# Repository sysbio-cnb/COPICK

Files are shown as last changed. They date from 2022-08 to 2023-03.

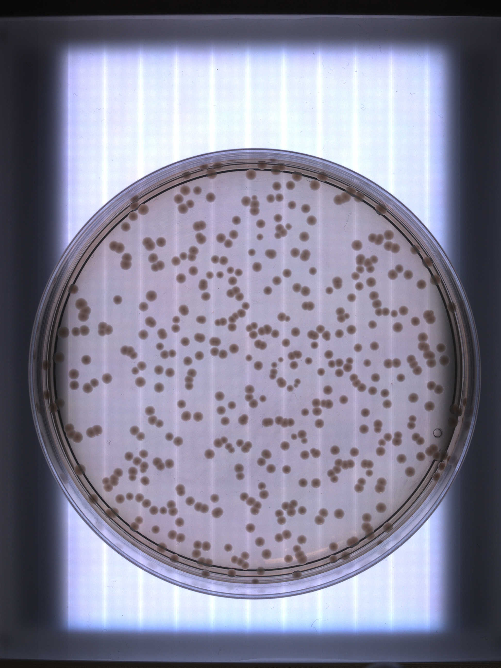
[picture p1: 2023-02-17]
Technical Validation/Raw picking test/ME3I_white__201222_132051.JPG

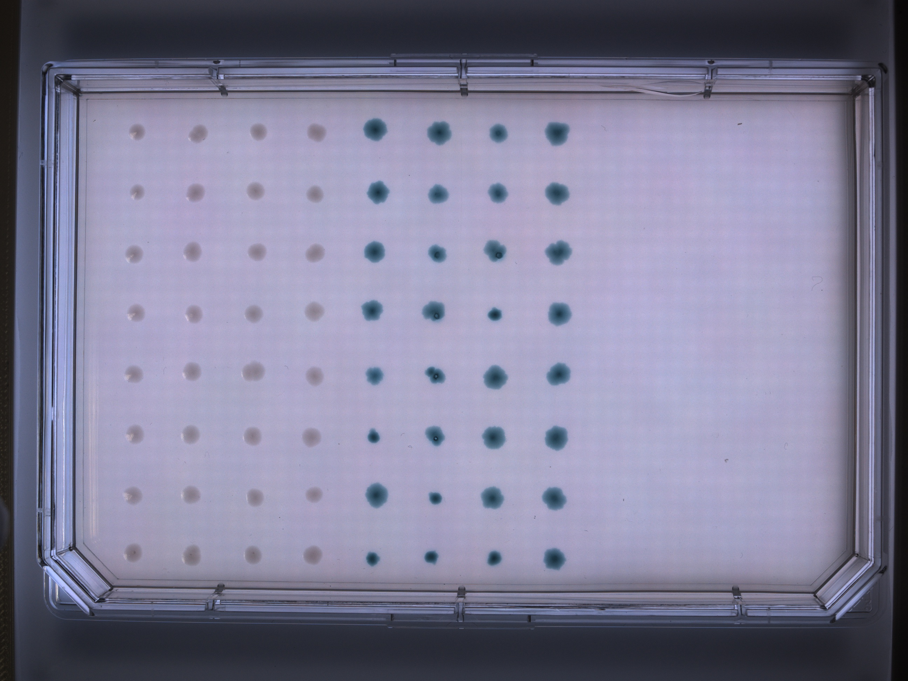
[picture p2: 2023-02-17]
Technical Validation/Color screening test/ME3I_white__310123_132437.JPG

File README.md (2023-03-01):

# COPICK: An open-source adaptation of Opentrons OT-2 robot to support colony picking  
Framework designed to adapt Opentrons 2 robot for colony picking protocols.

Colony picking is a labware based protocol involving the operation of several pieces of hardware in a unique sequence of tasks. The core of such workflow is the visual identification of colonies on the surface of agar plates. Although OT-2 is an open source platform exhibiting great operational capabilities, it lacks of any kind of computer vision recognition system. As a consequence, OT-2 cannot support colony picking.
COPICK package offers a technical solution to enable OT-2 as a colony picking platform at hardware and software level, spotting the two main problems in such task:

-	Computer vision of agar plates is performed using a convolutional neural network with an architecture proposed by Facebook research team (Detectron2, https://github.com/facebookresearch/detectron2), specifically trained with a “de novo” colony plate database. This database contains images of petri dishes with both M9 and LB agar containing P.putida and E.coli colonies.

-	The framework assembly to adapt OT-2 robot for colony picking operations. It includes CAD models for a custom-made scaffolding to assemble a DIY transilluminator (based on a cheap RGB LED matrix powered by a Raspberry Pi) and a high sensitivity USB color camera. The whole setup is complemented with all the scripts required to synchronize the image computation with robot movement and light activation, convert data gathered from the image to actual picking process and use typical filter criterion of colonies (size, color, GFP).

Information about both implementations can be found inside each respective folder.

# Citation

This project is also presented and explained in a formal published manuscript in BioRXiv: https://www.biorxiv.org/content/10.1101/2023.02.28.530165v1

# Contact

Questions and suggestions are kindly welcome. Feel free to contact us on david.rodriguez@cnb.csic.es

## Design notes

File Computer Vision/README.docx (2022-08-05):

COLONY COUNTING AND PICKING PACKAGE FOR OPENTRONS OT-2 (COPICK)

COMPUTER VISION ENGINE

This folder contains a purpose-made software package implementing the computer vision model required to analyze images of agar plates in order to identify bacterial colonies to pick. This package provides the hardware and software designs in different subfolders as described below:

- Light frame CAD designs: contains 3D models to build the photography setup structure for the acquisition of the images for the colony counting and picking dataset (COPICK dataset).
- Detectron2: the core of COPICK image recognition model. It contains the required libraries and scripts to work with a Convolutional Neural Network whose architecture was developed by Facebook research team. It is used to develop an inference model for colonies detection in agar plates. Scripts to set up the configuration for training, evaluation and optimization of the inference model are provided. Additionally, there are scripts to get and visualize model predictions.
- Dataset preparation: contains files related to the COPICK dataset preparation process. Scripts for image processing, segmentation, and automatic annotation and labelling are provided. There is also a *.json file template to be employed during the labelling step (json_template.json) and a *.csv file containing the dataset information (Colony_Picking_database.csv).
- Programs versions.pdf: listed employed programs versions to develop the colony counting and picking system.

DETECTRON2

An inference model for bacterial colonies detection in agar plates was developed using Detectron2, a Facebook AI Research’s library for Computer Vision tasks (https://github.com/facebookresearch/detectron2). It is built for Linux and macOS with Python and it works with PyTorch and torchvision as Machine Learning Framework.

Installation of Detectron2 library for Linux or macOS can be checked here: https://github.com/facebookresearch/detectron2.

Additional instructions on the installation of Detectron2 for Windows are specified in Detectron2_Windows.txt file (in Detectron2 folder). To build the colony detection model, Detectron2 for Windows with CPU only was used. A custom dataset for colony counting and picking purposes (COPICK dataset) was also created to train and evaluate the inference model.

From the different tasks Detectron2 offers, Panoptic Segmentation was chosen mainly because it allows segmentation of every pixel in an image¹. Considering the scenario in which the COPICK dataset is built (colonies are sometimes very numerous, similar and small objects to detect in an image), Panoptic Segmentation was thought to be a good approach in this particular case to get an accurate inference model for bacterial colonies detection. Panoptic Segmentation model and weights previously trained on the COCO dataset (https://cocodataset.org/#home) were used as a starting point. The employed model was the Panoptic R101-FPN (3x) and its corresponding model weights to be found in Detectron2 MODEL ZOO:

https://github.com/facebookresearch/detectron2/blob/main/MODEL_ZOO.md

To prepare and train the COPICK custom dataset, instructions on Detectron2 custom datasets and COCO dataset format for Panoptic FPN Segmentation models were followed:

- Detectron2 custom datasets format:

https://detectron2.readthedocs.io/en/latest/tutorials/datasets.html

- Detectron 2 Panoptic FPN for COCO format:

https://detectron2.readthedocs.io/en/latest/tutorials/builtin_datasets.html

- COCO dataset format:

https://cocodataset.org/#format-data

Overall, to prepare and register a custom dataset with COCO format for a Panoptic FPN model these are the files needed:

- Original images
- Annotations:
  - Panoptic masks (*.png annotations): masks in which every pixel is assigned to a segment in the image (each segment has a unique id).
  - Semantic masks (*.png annotations): refers to the stuff categories in the dataset (isthing=0), i.e. non-colonies objects in the image.
  - Panoptic JSON: includes panoptic segments annotations.
  - Instances JSON: includes things (isthing=1) segments annotations, i.e. colonies in the image.

There are different tools for image annotation and labeling, but the work has to be done manually in most cases for each object in the image. Therefore, traditional image processing techniques were used in order to generate automatic annotations of COPICK dataset. Instructions and scripts to generate the above files are detailed next in DATASET PREPARATION.

DATASET PREPARATION

1. Image acquisition

To prepare the bacterial colony counting and picking dataset (COPICK dataset), a total of 200 petri dishes with different conditions were collected from lab colleagues (Víctor de Lorenzo’s lab, CNB-CSIC). The plates included different bacteria species (either P. putida KT-2440 strain colonies or E. coli) and mediums such as LB or M9 minimal medium. Total number of colonies in each plate were previously counted and added to the plates. Empty plates only with medium were also added.

Before image acquisition, plate preparation data (i.e. agar composition, strain, etc.) was annotated and associated with a plate number. All of this information was stored in a database (Colony_Picking_database.csv, in Dataset preparation folder) containing the following fields:

- date: image capture date.
- id: image number in the dataset.
- filename: assigned name of image using the file_namer.py script in Dataset preparation folder.
- category: 0 for empty plates and 1 for plates with bacterial colonies.
- colonies: number of previously counted colonies in each plate.
- strain: None for empty plates, P. putida or E. coli for the rest of plates.
- medium: M9-cit (minimal M9 citrate medium) or LB.
- multicolor: 0 for plates with non-colored colonies and 1 for plates with colored colonies. This field was added for future additions to the dataset. In this case there were not plates with colored colonies.
- obs: plate observations.
- colonysize: general colonies size in the plate. Small, big or bigger categories.
- recount: number of colonies in plates after recounting some of them.

Image acquisition was performed with a Nikon reflex camera (model D60) with a macro lens (AF-S Micro NIKKOR 60 mm f/2.8G ED). To obtain good quality images, a custom-made illumination device was designed. It was composed by a led circular focus (123 mm, 6.7w, 1000 lumen) supported by a 3D holder designed using Autodesk Inventor Professional (2015) and printed with a Ultimaker³ 3D printer (see Figure 1). Two light diffusing layers of translucid plastic and paper were added to the assembly in order to attenuate the amount of light. Both 3D models can be found in the Light frame CAD designs folder.

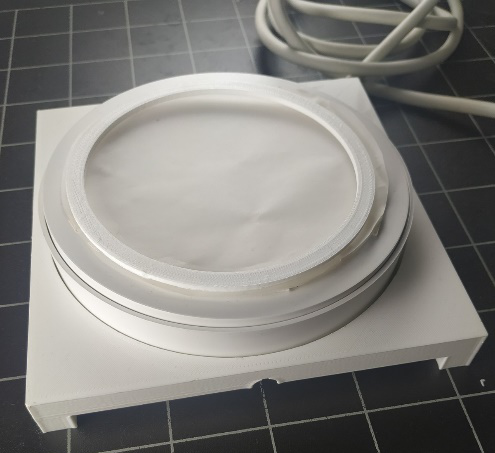
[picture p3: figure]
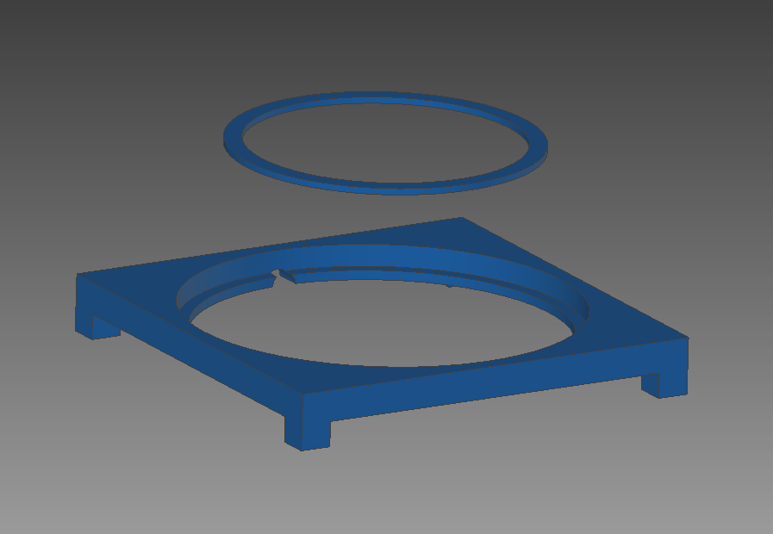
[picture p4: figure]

Figure 1. Led focus support structure and plates ring holder. a) 3D pieces design; b) final structure for image acquisition.

a

b

Images of the 200 collected plates were taken under the same conditions without lid for to avoid lines and reflections in the images.

2. Dataset augmentation

After image acquisition, dataset augmentation techniques were applied in order to increase the dataset size. Using the augmentation_stage.py script (in Dataset preparation folder), flip and rotation transformations were applied to the original set of images generating 15 replicas of each one and resulting in a total of 3000 images in the COPICK dataset. Every image was assigned a different name using the file_namer.py script (in Dataset preparation folder) during the augmentation process. Replicas of the same image share a common code at the beginning of their names for a better identification:

Code → A0000X, where the X corresponds to the assigned number of plate during image acquisition. Therefore, X values range from 1 to 200.

The 3000 images were divided in two subsets: train dataset (2250 images) and val dataset (750 images) for training and validation steps respectively. Previously mentioned database file (Colony_Picking_database.csv) contains the information of the whole augmented COPICK dataset.

3. Image processing and annotation

In order to produce panoptic and semantic annotations for each image in the dataset (as mentioned previously), two specific scripts (PROCESS_DATASET_PANOPTIC_SEGMENTATION.py and PROCESS_DATASET_INSTANCE_SEGMENTATION.py) and auxiliary functions were created (see Dataset preparation folder).

First, PROCESS_DATASET_PANOPTIC_SEGMENTATION.py was executed. In this script, the steps are:

1. Define dataset images paths and choose train or val datasets to be processed.
2. Then load and set fields to the provided json_template.json file (-json and csv files- folder in Dataset preparation folder) to store panoptic annotations.
3. Access database data (Colony_picking_database.csv in -json and csv files- in Dataset preparation folder) for panoptic segments annotations.
4. Define color combinations for panoptic *.png annotations.
5. Process dataset (train or val) to get panoptic annotations.
  5.1. Load images and create new folders to store panoptic *.png annotations.
  5.2. Call image_pretreatment.py function (in Dataset preparation folder) to crop images in order to avoid unnecessary regions and get region-based masks and data to be used in next segmentation steps.
  5.3. Call segmentation_stage.py function (in Dataset preparation folder) to generate final segmented panoptic masks *.png annotations.
  5.4. Store panoptic masks *.png annotations.
  5.5. Get panoptic segments annotations and store them in the json_template. Then save the *.json annotation file to specified folder.
6. Process dataset (train or val) to get semantic *.png annotations from panoptic *.png annotations.
  6.1. Access panoptic annotations (both *.png and *.json files) and create new paths to store semantic annotations.
  6.2. Define dataset categories and call modified Detectron2 function separate_semantic_from_panoptic.py (in Dataset preparation) to get and store semantic masks *.png annotations.

Then, PROCESS_DATASET_INSTANCE_SEGMENTATION.py script was executed to generate instances annotations. In this script the steps are:

1. Choose train or val dataset to process and load previously created panoptic *.json annotations.
2. Then load and set fields to the provided json_template.json file (-json and csv files- folder in Dataset preparation folder) to store instance annotations.
3. Process dataset (train or val) to get instance annotations from panoptic info.
4. Get instances annotations and store them in the json_template. Then save the *.json annotation file to specified folder.

Further explanation on each mentioned function can be found inside its respective script in the Dataset preparation folder.

DATASETS DESCRIPTION

COPICK dataset images and annotations files as well as some trial smaller datasets can be found in this repository to download:

https://sysbiol.cnb.csic.es/EMBBT

In the repository, the -Complete dataset (COPICK)- folder contains the images and annotations of the whole colony counting and picking dataset used to generate the final trained model on Detectron2 for bacterial colonies detection in agar plates. The original images from the whole dataset are stored and separated in "train" and "val" folders. The corresponding annotations of both datasets follow the Panoptic Segmentation format for Detectron2 with COCO dataset and PanopticFPN models previously described:

- *.json files for both panoptic and instances annotations: generated with -PROCESS_DATASET_PANOPTIC_SEGMENTATION.py- and -PROCESS_DATASET_INSTANCES_SEGMENTATION.py- scripts respectively (in Dataset preparation folder).
- *.png panoptic masks annotations: generated with -PROCESS_DATASET_PANOPTIC_SEGMENTATION.py- script (in Dataset preparation folder). Created for train and val datasets in -panoptic_trainval (panoptic annotations)- folder.
- *.png semantic mask annotations: generated from panoptic masks annotations with modified Detectron2 -prepare_panoptic_fpn.py- script (inside -PROCESS_DATASET_PANOPTIC_SEGMENTATION.py- script (in Dataset preparation folder). Created for train and val datasets in panoptic_stuff (semantic annotations) folder.

There is also a "Trial datasets" folder including smaller samples of the whole dataset following the same format as the complete dataset. These datasets are created in order to do faster testing with data. The folder includes:

- train_val_short: contains 10 training images and 3 validation images and corresponding annotations files.
- train_val_test_sample: contains 160 training images and 40 validation images and corresponding annotations files.
- val_short: contains 1 image for inference/validation only and corresponding annotations files.

DETECTRON2 CONFIGURATION

Some examples on Detectron2 configuration for training, evaluation and inference can be found in here:

https://colab.research.google.com/drive/16jcaJoc6bCFAQ96jDe2HwtXj7BMD_-m5

As Panoptic Segmentation is a relatively new task, there is not much available information nor examples on how to set up the configuration for training and evaluation purposes on custom datasets. Here is a list of additional resources that were consulted in order to set up Detectron2 to train with the COPICK dataset:

- Train Panoptic Segmentation model on custom dataset:

https://github.com/facebookresearch/detectron2/issues/1691

- Panoptic Segmentation dataset organization:

https://github.com/facebookresearch/detectron2/issues/1201#issuecomment-879864483

- Dataset registration:

https://github.com/facebookresearch/detectron2/issues/327

- Load custom datasets for evaluation:

https://github.com/facebookresearch/detectron2/issues/552

Additionally, based on information from the above sites and personal experience, changes were applied to some of the Detectron2 package scripts. Those can be found in -Changes in Detectron2 scripts.txt- file (in Detectron2 folder).

Detectron2 configuration setup scripts for training, evaluation, inference and optimization procedures are provided and detailed down below.

1. Training and Evaluation

Detectron2 configuration to train and evaluate the inference model on the COPICK dataset can be found in detectron2_train_eval.py script (in Train, evaluation and optimization folder from the Detectron2 folder). In this script, both train and val datasets are first registered with -register_coco_panoptic_separated- function from Detectron2. For the register, corresponding images and annotations files are required. After that, training configuration parameters are set to train the inference model on the COPICK dataset. Then, trained model weights are stored and evaluation parameters are set for evaluation, obtaining Panoptic Segmentation metrics (see https://cocodataset.org/#panoptic-eval).

2. Model Inference

Model inference can be done in different ways to check model predictions. Additionally to Detectron2 Visualizer function for registered datasets, scripts to get predicted colonies in the images and visualize them were created:

- detectron2_get_model_predictions.py: it is used to get predictions from the trained model and store them. Dataset registration is only necessary if Detectron2 Visualizer function is going to be used. If not, then just the trained model and weights as well as the test parameters are required to set the model predictor for inference. After that, multiple or single images can be processed in order to get and store panoptic predictions.
- display_colonies_overlay.py: it is used to process panoptic predictions to get only the colonies footprint and display an overlay of it on top of the original image for visualization purposes.

Both scripts can be found in the -Train, evaluation and optimization- folder (inside Detectron2 folder).

3. Hyperparameters optimization

To search for best hyperparameters combinations and improve the colony detection model accuracy, hyperparameter optimization techniques were used. For that purpose, the Optuna library was chosen (https://optuna.org/). By default, this library uses Bayesian Optimization algorithms but it can be changed if wanted.

The script -detectron2_optimization.py- (in Train, evaluation and optimization- folder from Detectron2 folder) is provided to perform hyperparameters optimization. The configuration of parameters values was done following Optuna’s instructions. In this case, the parameters to be optimized were:

- SOLVER.IMS_PER_BATCH: defined as number of images per batch across all machines.
- SOLVER.BASE_LR: learning rate.
- SOLVER.MAX_ITER: maximum number of iterations.
- MODEL.ROI_HEADS.BATCH_SIZE_PER_IMAGE: number of regions of interest per image during training.

Further information on Detectron2 configuration parameters can be found in here:

https://detectron2.readthedocs.io/en/latest/modules/config.html

Parameters to be optimized had to be included inside a function along with Detectron2 necessary configuration parameters for training and evaluation. This function returns a Panoptic Segmentation metric value SQ (Segmentation Quality) after evaluation to be maximized. The higher the SQ value is, the better the combination of hyperparameters of that optimization iteration are supposed to be to train the colony detection model and get more accurate predictions. Initially, PQ (Panoptic Quality) metric was used for optimization but better results were observed with SQ.

The hyperparameter optimization was performed by executing runs of 6 trials (n_trials) followed by the addition of the results to a *.pkl file as described in Optuna library to increase the number of data points in each batch and improve the accuracy of the next prediction. The reason of such procedure was a recurrent memory error that systematically interrupted the execution of larger optimization runs. We hypothesize that the issue is located at some point of inner memory allocation managed by torch libraries required to execute Detectron.

Once optimization was finished, best trained model weights both for PQ and SQ parameters were selected. These weights are provided in the above mentioned repository along with the COPICK dataset files.

LIMITATIONS AND ISSUES

Limitations about use, configuration and performance of the presented inference model are described next:

- Documentation: public documentation provided by both Detectron2 and COCO dataset regarding Panoptic Segmentation was found to be confusing at some points. The lack of information and examples on how to train Panoptic Segmentation models on custom datasets made it difficult to set the final configuration to train and evaluate our model and we ended up using a mix of different sources as mentioned before.
- COPICK dataset: the COPICK dataset was built using the most common conditions for plates preparation in the lab they were collected from. Those are not representative of other conditions and it has to be considered, even though Neural Networks models are very versatile and can discriminate different types of similar objects under variable circumstances. Also, light settings for image acquisition in the dataset are very important for a good image quality and we found our model to be very sensitive to light conditions when changing them inside the Opentrons robot. Finally, we considered the dataset size to be appropriate as a starting point. However, images with previously unincluded information such as different mediums or colonies fluorescence, color, and shape, as well as extra information on colonies size and number (regarding more information of groups of 2 or more colonies too), would be required to increase the dataset data and variability for the model to learn from and be more complete in the future.
- Image segmentation: image segmentation was probably the main problem to tackle when preparing the COPICK dataset annotations. We had to deal with difficult regions such as the border of the plates where the plastic is thicker and both the agar and the colonies often have a different morphology. Moreover, the agar is not a homogeneous medium: it has bubbles, wrinkles or traces of particles that add unspecific noise to the apparent uniformity of the plate. Therefore, light conditions vary in those regions even for the same agar composition. Additionally, plates with very small and hundreds of colonies had to be treated differently for a higher contrast of the colonies in the images in order to detect them. For those reasons, we had to consider all of the possible regions and cases to create the segmentation algorithm. We managed to segment as many colonies as possible in the dataset images, including the problematic ones, still the segmentation was not perfect as it is not a trivial task to perform and it conditioned the posterior model training.
- Memory usage: recurrent memory errors were found at some point during the inference model training and evaluation process and also during hyperparameters optimization. For the installation of Detectron2 and Pytorch we could not manage to set it up for GPU usage and therefore had to use only the CPU. This problem, as well as the inner memory allocation of torch libraries mentioned before, were limitations to build the inference model.
- Model inference results: after several training and optimization runs of the model, we observed it was good at segmentation but not that much at identification. This means it was accurate when segmenting every different object in an image, mainly varying on the contours of the segments from one training to another, but it worked worse when assigning a category to those segmented objects, in this case, the colonies. Hence, model predictions have some colonies classified as colonies and the rest only segmented and uncategorized. For our purposes, this is not a problem as we get the segmentation footprint of the colonies in the images anyway and that is enough to identify them and pick them. For the implementation of the colony picking application in the Opentrons, we ended up using a combination of the best trained model weights to get the best segmentation results possible.
- Model metrics: during evaluation, we found Panoptic Segmentation metrics to fail for the stuff categories as every metric value was always 0. We tried to solve this issue but we could not figure out what was causing it. Also, we observed during optimization that larger values of both PQ and SQ metrics were not necessarily correlated with a realistic prediction of colonies in the images at naked eye. As Panoptic Segmentation codes for evaluation task provided by COCO are relatively new and have been only tested on the COCO dataset (check https://cocodataset.org/#panoptic-eval), evaluation metrics and configuration might not be working well for our custom dataset and model.

REFERENCES

1. Panoptic Segmentation task paper: https://arxiv.org/abs/1801.00868

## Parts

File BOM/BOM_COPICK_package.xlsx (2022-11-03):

Concept | Supplier | Ref | Units
Raspberry Pi 4B , 8GB, bulk | Mouser | 358-RPI4MODBP8GBBULK | 1
USB 3.0 Micro-B to Type-A Locking Cable, 3m | Edmund Optics | #14-903 | 1
Hoya Y50 (500nm), 25.4mm Dia., 2.5mm Thick, Colored Glass Longpass Filter | Edmund Optics | #66-050 | 1
Allied Vision Alvium 1800 U-500c, 1/2.5" 5.0MP C-Mount, Right Angle USB 3.1 Color Camera | Edmund Optics | #14-131 | 1
12mm UC Series Fixed Focal Length Lens | Edmund Optics | #33-303 | 1
Mount M25.5 x 0.5 for 25/25.4mm Diameter Filters | Edmund Optics | #65-800 | 1
64X32 RGB LED MATRIX - 2.5MM PIT | Digikey | 1528-5036-ND | 1
5V AC/DC Externo Escritorio (Clase II) Adaptador Cable Entrada | Digikey | 1528-1466AD-ND | 1
6.00' (1.83m) Cable de alimentación Negro CEE 7/16 a IEC 320-C7 SPT-2 | Digikey | T1167-EU-ND | 1
LED MATRIX RGB HAT RTC RASP PI | Digikey | 1528-1432-ND | 1
MINI-MAGNET FEET FOR RGB LED MAT | Digikey | 1528-4631-ND | 1
3D printed parts | - | -
M3 screws (12 mm) | RS amidata | 190-456 | 1
M3 nuts | RS amidata | 189-563 | 1
M4 screws (20 mm) | RS amidata | 227-6849 | 1
M4 nuts | RS amidata | 189-579 | 1
Bosch Rexroth Connecting Component, Angle Bracket, strut profile 20 mm, groove Size 6mm | RS amidata | 466-7354 | 1
Light diffusor: PETG or PE plate , 5 mm width | - | - | 1
Light diffusor 2: PETG or PE plate , 5 mm width | - | - | 1
CAT 5 / CAT 6 Ethernet cable | Digikey | AE10365-ND | 1
8 port switch, TP-link TL-SG108E | Amazon | TL-SG108E | 1
wall charger usb 3.0, 2A | Amazon |  | 1
16 GB SD card | Amazon |  | 1

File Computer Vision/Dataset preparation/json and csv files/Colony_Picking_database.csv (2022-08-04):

date | id | filename | category | colonies | strain | medium | multicolor | obs | colonysize | recount
16/09/2021 | 1 | A0000125pa5gr2idie3f2bv4kupalr1.jpg | 0 | 0 | None | M9_cit | 0 |  | big
16/09/2021 | 2 | A000015fnp53868wk181oa8q35bhdfj.jpg | 0 | 0 | None | M9_cit | 0 |  | big
16/09/2021 | 3 | A000017blexsmxpoldrkko23xwipyb0.jpg | 0 | 0 | None | M9_cit | 0 |  | big
16/09/2021 | 4 | A00001bgvr54etcrd66lmu3dhparv5a.jpg | 0 | 0 | None | M9_cit | 0 |  | big
16/09/2021 | 5 | A00001cvlner9f6ccik1m3yzgx7euby.jpg | 0 | 0 | None | M9_cit | 0 |  | big
16/09/2021 | 6 | A00001g55zyv68qmezpfr794x4itvl6.jpg | 0 | 0 | None | M9_cit | 0 |  | big
16/09/2021 | 7 | A00001gxaz519m72og3gcu8e3wbg2x7.jpg | 0 | 0 | None | M9_cit | 0 |  | big
16/09/2021 | 8 | A00001ifallx9e1vcrpj0xz2v2l1bvc.jpg | 0 | 0 | None | M9_cit | 0 |  | big
16/09/2021 | 9 | A00001mre7wa8a446zoo3rdja20u31s.jpg | 0 | 0 | None | M9_cit | 0 |  | big
16/09/2021 | 10 | A00001qtv38wa1q83zlr5pooi141w1s.jpg | 0 | 0 | None | M9_cit | 0 |  | big
16/09/2021 | 11 | A00001sz8bqkzq0zr17lmxunfps6ii2.jpg | 0 | 0 | None | M9_cit | 0 |  | big
16/09/2021 | 12 | A00001w7halk3oyksxyvznr5q3vem3y.jpg | 0 | 0 | None | M9_cit | 0 |  | big
16/09/2021 | 13 | A00001wezej7ya386otummtlp9r6cru.jpg | 0 | 0 | None | M9_cit | 0 |  | big
16/09/2021 | 14 | A00001xaznw266ws5k6cgpv5f7s8bty.jpg | 0 | 0 | None | M9_cit | 0 |  | big
16/09/2021 | 15 | A00001yxv8zs82ltzsjoyv6see0uzq9.jpg | 0 | 0 | None | M9_cit | 0 |  | big
16/09/2021 | 16 | A000021brca8pix0p1475vr33a17k5u.jpg | 1 | 91 | P. putida | M9_cit | 0 |  | big
16/09/2021 | 17 | A0000231324ioer85ijegxmg743lynn.jpg | 1 | 91 | P. putida | M9_cit | 0 |  | big
16/09/2021 | 18 | A000023ls3ta6ttl0iw7gp83msg57e6.jpg | 1 | 91 | P. putida | M9_cit | 0 |  | big
16/09/2021 | 19 | A000025huv9kxjn3hza0xxqhslwt4tc.jpg | 1 | 91 | P. putida | M9_cit | 0 |  | big
16/09/2021 | 20 | A000027zrqi3aezz9lt2siq9bohwc1u.jpg | 1 | 91 | P. putida | M9_cit | 0 |  | big
16/09/2021 | 21 | A00002c5lj73313kpz424rsuq10e4q8.jpg | 1 | 91 | P. putida | M9_cit | 0 |  | big
16/09/2021 | 22 | A00002d2kilfobrbq5erai8pm2nczjb.jpg | 1 | 91 | P. putida | M9_cit | 0 |  | big
16/09/2021 | 23 | A00002eu1a3ge3aj789mj2eh8akqsnt.jpg | 1 | 91 | P. putida | M9_cit | 0 |  | big
16/09/2021 | 24 | A00002gfkyesf41a8ujvz2gcisccghz.jpg | 1 | 91 | P. putida | M9_cit | 0 |  | big
16/09/2021 | 25 | A00002h8ahvgqjvwi5bgns6dtg5mvg5.jpg | 1 | 91 | P. putida | M9_cit | 0 |  | big
16/09/2021 | 26 | A00002hz0y2816vvoq3n15b63cb3r95.jpg | 1 | 91 | P. putida | M9_cit | 0 |  | big
16/09/2021 | 27 | A00002o8nzisdk3og1lgybj9nul7m2m.jpg | 1 | 91 | P. putida | M9_cit | 0 |  | big
16/09/2021 | 28 | A00002pexrmshcmz9fzknj9c2y0pbxq.jpg | 1 | 91 | P. putida | M9_cit | 0 |  | big
16/09/2021 | 29 | A00002s6w3asd0zikiqqovcobhgxsu8.jpg | 1 | 91 | P. putida | M9_cit | 0 |  | big
16/09/2021 | 30 | A00002t4lgaor1idwmcnbi8oryhz8ri.jpg | 1 | 91 | P. putida | M9_cit | 0 |  | big
16/09/2021 | 31 | A000032ymuivkqisok7bm7891ztwntg.jpg | 1 | 67 | P. putida | M9_cit | 0 |  | big
16/09/2021 | 32 | A0000374xgg3faz8ut9x8f6aczsb6qh.jpg | 1 | 67 | P. putida | M9_cit | 0 |  | big
16/09/2021 | 33 | A0000395f2kwbakbi86kip7z0cwggr9.jpg | 1 | 67 | P. putida | M9_cit | 0 |  | big
16/09/2021 | 34 | A00003aorrz6rcrujqomgfuv6fouedk.jpg | 1 | 67 | P. putida | M9_cit | 0 |  | big
16/09/2021 | 35 | A00003cu8bvasxy3lp20k4n38s869bj.jpg | 1 | 67 | P. putida | M9_cit | 0 |  | big
16/09/2021 | 36 | A00003g04g2zppox5vhxbqu7tosb67a.jpg | 1 | 67 | P. putida | M9_cit | 0 |  | big
16/09/2021 | 37 | A00003g4yhn60qh7xjws63nx556gg4x.jpg | 1 | 67 | P. putida | M9_cit | 0 |  | big
16/09/2021 | 38 | A00003jbotnyz71n5t7xv4acuthk7u1.jpg | 1 | 67 | P. putida | M9_cit | 0 |  | big
16/09/2021 | 39 | A00003kezhrbni3j1h5gj8atr6h850t.jpg | 1 | 67 | P. putida | M9_cit | 0 |  | big
16/09/2021 | 40 | A00003kqah2dnhuiiknxlefynu79fsr.jpg | 1 | 67 | P. putida | M9_cit | 0 |  | big
16/09/2021 | 41 | A00003l9jtmyozxsxcr4c7f4o7tsj3x.jpg | 1 | 67 | P. putida | M9_cit | 0 |  | big
16/09/2021 | 42 | A00003mrs477xdbh95su65uvpr7euo1.jpg | 1 | 67 | P. putida | M9_cit | 0 |  | big
16/09/2021 | 43 | A00003npkb798j1i5nn0evttn6wmlwh.jpg | 1 | 67 | P. putida | M9_cit | 0 |  | big
16/09/2021 | 44 | A00003nrk93x3oosyeb151gmzmvinui.jpg | 1 | 67 | P. putida | M9_cit | 0 |  | big
16/09/2021 | 45 | A00003yg3tagqbshz716acr2w9wfxwg.jpg | 1 | 67 | P. putida | M9_cit | 0 |  | big
16/09/2021 | 46 | A000042hhjzcwvflnjxzktp0is7ps99.jpg | 1 | 44 | P. putida | M9_cit | 0 |  | big
16/09/2021 | 47 | A0000437ugpshij4g5vsrnlno8wuufs.jpg | 1 | 44 | P. putida | M9_cit | 0 |  | big
16/09/2021 | 48 | A000044d9jqi8hq7zaeu8ibigm9s418.jpg | 1 | 44 | P. putida | M9_cit | 0 |  | big
16/09/2021 | 49 | A000044e1qrgd3sa1hqr4a7mi7m54yb.jpg | 1 | 44 | P. putida | M9_cit | 0 |  | big
16/09/2021 | 50 | A000046dfkyg6t78mnbk4iyxoda93h0.jpg | 1 | 44 | P. putida | M9_cit | 0 |  | big
16/09/2021 | 51 | A0000482je8nzs00hz4e595r0p0b3m2.jpg | 1 | 44 | P. putida | M9_cit | 0 |  | big
16/09/2021 | 52 | A000049r7jflirf4mq6x8dnomlogj5a.jpg | 1 | 44 | P. putida | M9_cit | 0 |  | big
16/09/2021 | 53 | A00004an08qaig3t867aj8vu3kp51f8.jpg | 1 | 44 | P. putida | M9_cit | 0 |  | big
16/09/2021 | 54 | A00004ga5xno45lsqdqwoevjvyr3xjf.jpg | 1 | 44 | P. putida | M9_cit | 0 |  | big
16/09/2021 | 55 | A00004gijackmbgpe2nc0adu2gu1tyq.jpg | 1 | 44 | P. putida | M9_cit | 0 |  | big
16/09/2021 | 56 | A00004jzaaaer9h64dyvmgam3tx9b4z.jpg | 1 | 44 | P. putida | M9_cit | 0 |  | big
16/09/2021 | 57 | A00004m6kwbwc0g92iqql2hn9f4bvq9.jpg | 1 | 44 | P. putida | M9_cit | 0 |  | big
16/09/2021 | 58 | A00004u95rhb57ran6lu1nbi0lfdbt1.jpg | 1 | 44 | P. putida | M9_cit | 0 |  | big
16/09/2021 | 59 | A00004ylrp7ok6kurz6jl8qa97kqe1h.jpg | 1 | 44 | P. putida | M9_cit | 0 |  | big
16/09/2021 | 60 | A00004z5e1ir6lttwwbdejkvo7p2bky.jpg | 1 | 44 | P. putida | M9_cit | 0 |  | big
16/09/2021 | 61 | A000050342kk9oekqj7twtarskonerp.jpg | 1 | 85 | P. putida | M9_cit | 0 |  | big
16/09/2021 | 62 | A000050i6x8vel5xk7r3p2zlc3uk93s.jpg | 1 | 85 | P. putida | M9_cit | 0 |  | big
16/09/2021 | 63 | A000052j5t6fggvnd4idya6l5li4bqs.jpg | 1 | 85 | P. putida | M9_cit | 0 |  | big
16/09/2021 | 64 | A000056mijhp79eao8lza8w0qejw9po.jpg | 1 | 85 | P. putida | M9_cit | 0 |  | big
16/09/2021 | 65 | A00005a75fp8l23fzcvo6w4qm37423i.jpg | 1 | 85 | P. putida | M9_cit | 0 |  | big
16/09/2021 | 66 | A00005d9s6bej7g9ngl2oo3e0zjfvh1.jpg | 1 | 85 | P. putida | M9_cit | 0 |  | big
16/09/2021 | 67 | A00005f5flv8idwruz42iadtk1bl6ai.jpg | 1 | 85 | P. putida | M9_cit | 0 |  | big
16/09/2021 | 68 | A00005f88s7oipyct4024qqpv1h9a9r.jpg | 1 | 85 | P. putida | M9_cit | 0 |  | big
16/09/2021 | 69 | A00005glwuv5q1tx884t0a1nf85b2k4.jpg | 1 | 85 | P. putida | M9_cit | 0 |  | big
16/09/2021 | 70 | A00005s95dzw3215dyctjmt83j8n1ho.jpg | 1 | 85 | P. putida | M9_cit | 0 |  | big
16/09/2021 | 71 | A00005vs0kxztnehei6iw2o09s7aros.jpg | 1 | 85 | P. putida | M9_cit | 0 |  | big
16/09/2021 | 72 | A00005w5fnqtr7luw2rr8zmumg9z6ay.jpg | 1 | 85 | P. putida | M9_cit | 0 |  | big
16/09/2021 | 73 | A00005wijjqw57hrot0oiy5m0dil7qy.jpg | 1 | 85 | P. putida | M9_cit | 0 |  | big
16/09/2021 | 74 | A00005xyo7dw6j2vjsj7ej0136v6fbz.jpg | 1 | 85 | P. putida | M9_cit | 0 |  | big
16/09/2021 | 75 | A00005y06r1a339ujnia2bsui16l9vh.jpg | 1 | 85 | P. putida | M9_cit | 0 |  | big
16/09/2021 | 76 | A0000615xod6tfueju6ek0szasbcu13.jpg | 1 | 115 | P. putida | M9_cit | 0 |  | big
16/09/2021 | 77 | A000061c4alfy0mzbb3i7ehxtv3vht5.jpg | 1 | 115 | P. putida | M9_cit | 0 |  | big
16/09/2021 | 78 | A000061ow6v7kmqm1dh34cocrowkddu.jpg | 1 | 115 | P. putida | M9_cit | 0 |  | big
16/09/2021 | 79 | A000063pz404fdu9oixn71n4r8rq5td.jpg | 1 | 115 | P. putida | M9_cit | 0 |  | big
16/09/2021 | 80 | A000065452lf4lj85f8go2qmahtkzow.jpg | 1 | 115 | P. putida | M9_cit | 0 |  | big
16/09/2021 | 81 | A000066xbkxe54pn8c2iujqdkd4ucum.jpg | 1 | 115 | P. putida | M9_cit | 0 |  | big
16/09/2021 | 82 | A000069nkdxkv5gnxm8n0x1sfmaye04.jpg | 1 | 115 | P. putida | M9_cit | 0 |  | big
16/09/2021 | 83 | A00006bgsulgrg4359gv3shhpjfoymd.jpg | 1 | 115 | P. putida | M9_cit | 0 |  | big
16/09/2021 | 84 | A00006ckv6jnf8l3ibh2z91ecpzdzqb.jpg | 1 | 115 | P. putida | M9_cit | 0 |  | big
16/09/2021 | 85 | A00006jr2i3a0u8f2b7zcups6zlewxn.jpg | 1 | 115 | P. putida | M9_cit | 0 |  | big
16/09/2021 | 86 | A00006kwizdvby50c150s9tuo3xqbbb.jpg | 1 | 115 | P. putida | M9_cit | 0 |  | big
16/09/2021 | 87 | A00006qex7u5f2vazey59cfs9u75v3a.jpg | 1 | 115 | P. putida | M9_cit | 0 |  | big
16/09/2021 | 88 | A00006uh6iw34gt54uekvy2fp905eb4.jpg | 1 | 115 | P. putida | M9_cit | 0 |  | big
16/09/2021 | 89 | A00006w8eab1yk8a8iodfev4byz1ylg.jpg | 1 | 115 | P. putida | M9_cit | 0 |  | big
16/09/2021 | 90 | A00006zohsu6su3h4pj9ljx73ozotj0.jpg | 1 | 115 | P. putida | M9_cit | 0 |  | big
16/09/2021 | 91 | A0000700szxmpryrtmkma7a0xr2u26v.jpg | 1 | 1 | P. putida | M9_cit | 0 |  | big
16/09/2021 | 92 | A000073hul1rhn14iita59rfzi4bgb4.jpg | 1 | 1 | P. putida | M9_cit | 0 |  | big
16/09/2021 | 93 | A000074dpl4uyihwqb8rnx1o7kwd6oo.jpg | 1 | 1 | P. putida | M9_cit | 0 |  | big
16/09/2021 | 94 | A000079ygs7q7lhf0q3sz03xwhss7lc.jpg | 1 | 1 | P. putida | M9_cit | 0 |  | big
16/09/2021 | 95 | A00007e3vllczp2t624gmpqfstd2k8b.jpg | 1 | 1 | P. putida | M9_cit | 0 |  | big
16/09/2021 | 96 | A00007gokdd3b2unkdky613imgg5w7f.jpg | 1 | 1 | P. putida | M9_cit | 0 |  | big
16/09/2021 | 97 | A00007hb846e2on6i4mnc1u03fd8qir.jpg | 1 | 1 | P. putida | M9_cit | 0 |  | big
16/09/2021 | 98 | A00007jyph6tawkyor43s0ohrd8ksi4.jpg | 1 | 1 | P. putida | M9_cit | 0 |  | big
16/09/2021 | 99 | A00007ly6rfdixi73ee4tr3ey6vlwai.jpg | 1 | 1 | P. putida | M9_cit | 0 |  | big
16/09/2021 | 100 | A00007mt2z19t1qyv4209ic1a6xq5hd.jpg | 1 | 1 | P. putida | M9_cit | 0 |  | big
16/09/2021 | 101 | A00007ncq16nc67aqpyfu1h589tls2s.jpg | 1 | 1 | P. putida | M9_cit | 0 |  | big
16/09/2021 | 102 | A00007q8cngkmb99etdsl6kyax5phbi.jpg | 1 | 1 | P. putida | M9_cit | 0 |  | big
16/09/2021 | 103 | A00007vkv0ytaady1vtdbnn2kn0oupn.jpg | 1 | 1 | P. putida | M9_cit | 0 |  | big
16/09/2021 | 104 | A00007ybnnsgt7dtcpvtd9mexi2y18o.jpg | 1 | 1 | P. putida | M9_cit | 0 |  | big
16/09/2021 | 105 | A00007yd1kenzh9uzlu8f33k2aie8n7.jpg | 1 | 1 | P. putida | M9_cit | 0 |  | big
16/09/2021 | 106 | A00008173vpw134effvc4xy2n7d8h8l.jpg | 1 | 132 | P. putida | M9_cit | 0 |  | big
16/09/2021 | 107 | A0000819zvokpwb3igj4exnif5xgi5l.jpg | 1 | 132 | P. putida | M9_cit | 0 |  | big
16/09/2021 | 108 | A000081aamy6o8yzi65ovv1mwd690y4.jpg | 1 | 132 | P. putida | M9_cit | 0 |  | big
16/09/2021 | 109 | A000082532llt26xoqeq9zuv7s0gewe.jpg | 1 | 132 | P. putida | M9_cit | 0 |  | big
16/09/2021 | 110 | A000082bc0bhfjbs47d9t2qj2risqzt.jpg | 1 | 132 | P. putida | M9_cit | 0 |  | big
16/09/2021 | 111 | A000082zejwqp5sg3lzceub1d8nttrp.jpg | 1 | 132 | P. putida | M9_cit | 0 |  | big
16/09/2021 | 112 | A000085zv53pajihcz5n17be8h6kc7q.jpg | 1 | 132 | P. putida | M9_cit | 0 |  | big
16/09/2021 | 113 | A00008d8ebhe73qfqmfk6lt6fu2fudp.jpg | 1 | 132 | P. putida | M9_cit | 0 |  | big
16/09/2021 | 114 | A00008fffh7fbxn2kjwt0isqewwgbcm.jpg | 1 | 132 | P. putida | M9_cit | 0 |  | big
16/09/2021 | 115 | A00008g1slffkn9jdgsc2epcw86xzfq.jpg | 1 | 132 | P. putida | M9_cit | 0 |  | big
16/09/2021 | 116 | A00008kp8fdy7dbnkaq1jaft31sm71y.jpg | 1 | 132 | P. putida | M9_cit | 0 |  | big
16/09/2021 | 117 | A00008lygbnlaqpfgqms90ym1lo946g.jpg | 1 | 132 | P. putida | M9_cit | 0 |  | big
16/09/2021 | 118 | A00008t4aq3iz9j8po1fi2muxikbduk.jpg | 1 | 132 | P. putida | M9_cit | 0 |  | big
16/09/2021 | 119 | A00008tpwa6t4zb9k86exzkf83v2i2q.jpg | 1 | 132 | P. putida | M9_cit | 0 |  | big
16/09/2021 | 120 | A00008zd1pqjgl207otzm0qt30ny2i1.jpg | 1 | 132 | P. putida | M9_cit | 0 |  | big
16/09/2021 | 121 | A000090ihyeacfms8yb5h22rhii60hg.jpg | 1 | 47 | P. putida | M9_cit | 0 |  | big
16/09/2021 | 122 | A000094gy3nsmi8h9hhcgw72gina10g.jpg | 1 | 47 | P. putida | M9_cit | 0 |  | big
16/09/2021 | 123 | A00009667ppu7lz5bbrbzggqg2wjuww.jpg | 1 | 47 | P. putida | M9_cit | 0 |  | big
16/09/2021 | 124 | A000096g29oqykt3paiadr63ykyj8lw.jpg | 1 | 47 | P. putida | M9_cit | 0 |  | big
16/09/2021 | 125 | A000098rzekftcg9zuj1rpyemwp2f7h.jpg | 1 | 47 | P. putida | M9_cit | 0 |  | big
16/09/2021 | 126 | A00009aq8y9lz1eitb94gbbdkitu1gs.jpg | 1 | 47 | P. putida | M9_cit | 0 |  | big
16/09/2021 | 127 | A00009in2ubyuk3ivgbdumeq4tj1uss.jpg | 1 | 47 | P. putida | M9_cit | 0 |  | big
16/09/2021 | 128 | A00009su3bkhjxuqigohekribcd9xor.jpg | 1 | 47 | P. putida | M9_cit | 0 |  | big
16/09/2021 | 129 | A00009u669kfgq0zz49fwamn1pjdxxs.jpg | 1 | 47 | P. putida | M9_cit | 0 |  | big
16/09/2021 | 130 | A00009w7hetnfjut3eggvanuwrnurbq.jpg | 1 | 47 | P. putida | M9_cit | 0 |  | big
16/09/2021 | 131 | A00009wcp1iubov46ju6i04nifttjd6.jpg | 1 | 47 | P. putida | M9_cit | 0 |  | big
16/09/2021 | 132 | A00009wm85mzptn0tp0gvibcdqoktlj.jpg | 1 | 47 | P. putida | M9_cit | 0 |  | big
16/09/2021 | 133 | A00009xn3n7dlsr4m2s4mpacf8uzj4x.jpg | 1 | 47 | P. putida | M9_cit | 0 |  | big
16/09/2021 | 134 | A00009ymuyd1kufiznfjup244bhn79x.jpg | 1 | 47 | P. putida | M9_cit | 0 |  | big
16/09/2021 | 135 | A00009z0azsae30pmgmytebflfo0342.jpg | 1 | 47 | P. putida | M9_cit | 0 |  | big
23/09/2021 | 136 | A00010365te8uvj554j8f399jnr1xj0.jpg | 1 | 65 | P. putida | M9_cit | 0 |  | big
23/09/2021 | 137 | A0001052shew0uwo4wq2beuf1bcvncr.jpg | 1 | 65 | P. putida | M9_cit | 0 |  | big
23/09/2021 | 138 | A0001066mb2g4hc2xw83x72z6myghge.jpg | 1 | 65 | P. putida | M9_cit | 0 |  | big
23/09/2021 | 139 | A00010826frrgmlqn1k62l69xyl3kep.jpg | 1 | 65 | P. putida | M9_cit | 0 |  | big
23/09/2021 | 140 | A000109mj3tbiu0rw4d73v827strukq.jpg | 1 | 65 | P. putida | M9_cit | 0 |  | big
23/09/2021 | 141 | A00010bkepiggmbj6ori2zbkz9r51ow.jpg | 1 | 65 | P. putida | M9_cit | 0 |  | big
23/09/2021 | 142 | A00010frjhdzahg1jzwllspqkrkqgmk.jpg | 1 | 65 | P. putida | M9_cit | 0 |  | big
23/09/2021 | 143 | A00010hj6b4217usxl3lyg1ua981aos.jpg | 1 | 65 | P. putida | M9_cit | 0 |  | big
23/09/2021 | 144 | A00010hqsru4drqnsdn0igx5ao2t2vy.jpg | 1 | 65 | P. putida | M9_cit | 0 |  | big
23/09/2021 | 145 | A00010jxa2o9t2az36kdiur0jndnwgk.jpg | 1 | 65 | P. putida | M9_cit | 0 |  | big
23/09/2021 | 146 | A00010k1bmpmih5crx957u4s8p1ztza.jpg | 1 | 65 | P. putida | M9_cit | 0 |  | big
23/09/2021 | 147 | A00010lo5usslo3jubrv71kyqgf4hw6.jpg | 1 | 65 | P. putida | M9_cit | 0 |  | big
23/09/2021 | 148 | A00010o5nkxbsmb14xt9m4pzhttwbyc.jpg | 1 | 65 | P. putida | M9_cit | 0 |  | big
23/09/2021 | 149 | A00010sla29pl9wex92m0a9nka64a74.jpg | 1 | 65 | P. putida | M9_cit | 0 |  | big
23/09/2021 | 150 | A00010tzomfat7z0ekvkajk2yrinb9v.jpg | 1 | 65 | P. putida | M9_cit | 0 |  | big
20/09/2021 | 151 | A00011330jvstu1nomkzw8g82ydxdch.jpg | 1 | 60 | P. putida | M9_cit | 0 |  | big
20/09/2021 | 152 | A000116g1c8bgin4stuumzoa9go3hx5.jpg | 1 | 60 | P. putida | M9_cit | 0 |  | big
20/09/2021 | 153 | A000118xvnjnq2zvix6gajlotz50keq.jpg | 1 | 60 | P. putida | M9_cit | 0 |  | big
20/09/2021 | 154 | A000119a3nwlyc7ppep7v2yb0w3otka.jpg | 1 | 60 | P. putida | M9_cit | 0 |  | big
20/09/2021 | 155 | A000119sykz62erzlqudy3o20g770c1.jpg | 1 | 60 | P. putida | M9_cit | 0 |  | big
20/09/2021 | 156 | A00011amba9dbihkljduzqf0w80x0bk.jpg | 1 | 60 | P. putida | M9_cit | 0 |  | big
20/09/2021 | 157 | A00011by9uoog44jrzz5lrxutlo3ajl.jpg | 1 | 60 | P. putida | M9_cit | 0 |  | big
20/09/2021 | 158 | A00011ixqsfjs4zgalxnih3nsn2a66r.jpg | 1 | 60 | P. putida | M9_cit | 0 |  | big
20/09/2021 | 159 | A00011jnp0ap0v1hmyo8m1w78q57eyl.jpg | 1 | 60 | P. putida | M9_cit | 0 |  | big
20/09/2021 | 160 | A00011masm7u1w08r1jqj2j0ahmfnuh.jpg | 1 | 60 | P. putida | M9_cit | 0 |  | big
20/09/2021 | 161 | A00011och24sj5trp18mpc5fkq59ccp.jpg | 1 | 60 | P. putida | M9_cit | 0 |  | big
20/09/2021 | 162 | A00011ohbo8yu3upvuk41iu4wr685ws.jpg | 1 | 60 | P. putida | M9_cit | 0 |  | big
20/09/2021 | 163 | A00011tjx3ign2p9dne3bvqqw2s0ik8.jpg | 1 | 60 | P. putida | M9_cit | 0 |  | big
20/09/2021 | 164 | A00011wdb6ozdmlsbcoyvf4xmrw4i7l.jpg | 1 | 60 | P. putida | M9_cit | 0 |  | big
20/09/2021 | 165 | A00011x2m9in2tqq7spg5q38wayvoa0.jpg | 1 | 60 | P. putida | M9_cit | 0 |  | big
20/09/2021 | 166 | A000122dyywbxlhovfnivc9bplxla1w.jpg | 1 | 6 | P. putida | M9_cit | 0 |  | big
20/09/2021 | 167 | A0001263stj64fe94mhra7h1v7yk1i2.jpg | 1 | 6 | P. putida | M9_cit | 0 |  | big
20/09/2021 | 168 | A000129w26c1tdaglxwigax9isquagk.jpg | 1 | 6 | P. putida | M9_cit | 0 |  | big
20/09/2021 | 169 | A00012b14w6vbeurkj9y0ompmy1dj0s.jpg | 1 | 6 | P. putida | M9_cit | 0 |  | big
20/09/2021 | 170 | A00012byiz7yti7kviinla0392sald2.jpg | 1 | 6 | P. putida | M9_cit | 0 |  | big
20/09/2021 | 171 | A00012dt350cbfspdecf65qk2wt4014.jpg | 1 | 6 | P. putida | M9_cit | 0 |  | big
20/09/2021 | 172 | A00012eyqao05tpsjaoqqy2g38uzt7h.jpg | 1 | 6 | P. putida | M9_cit | 0 |  | big
20/09/2021 | 173 | A00012gzblblpt5ib5buktvm6ibipzl.jpg | 1 | 6 | P. putida | M9_cit | 0 |  | big
20/09/2021 | 174 | A00012kc9zddk866dmhyvbbai8h7c29.jpg | 1 | 6 | P. putida | M9_cit | 0 |  | big
20/09/2021 | 175 | A00012mi1b8e5tgfbun1xsr88371yi5.jpg | 1 | 6 | P. putida | M9_cit | 0 |  | big
20/09/2021 | 176 | A00012obwe4zsnts57lke73bhqo22jt.jpg | 1 | 6 | P. putida | M9_cit | 0 |  | big
20/09/2021 | 177 | A00012qn4ph4d3b1x5l45g4ohy19av1.jpg | 1 | 6 | P. putida | M9_cit | 0 |  | big
20/09/2021 | 178 | A00012s6ik0ofrxlqm2d5wnjh9lgzst.jpg | 1 | 6 | P. putida | M9_cit | 0 |  | big
20/09/2021 | 179 | A00012xn1vovlvscahsqb4bkqw6eh08.jpg | 1 | 6 | P. putida | M9_cit | 0 |  | big
20/09/2021 | 180 | A00012yn9ulm69pvsise05uogfku7o7.jpg | 1 | 6 | P. putida | M9_cit | 0 |  | big
20/09/2021 | 181 | A000137viag4ibfuh1i01tbflk6ytmh.jpg | 1 | 46 | P. putida | M9_cit | 0 |  | big
20/09/2021 | 182 | A00013c9mkh4s6ppuywv3row1limxp5.jpg | 1 | 46 | P. putida | M9_cit | 0 |  | big
20/09/2021 | 183 | A00013dk9gdpzfjq9viqdfo2pkadkwq.jpg | 1 | 46 | P. putida | M9_cit | 0 |  | big
20/09/2021 | 184 | A00013dkwv8cbt0nspofmlvl19dp8xv.jpg | 1 | 46 | P. putida | M9_cit | 0 |  | big
20/09/2021 | 185 | A00013f5bgaxphp936pm5ykrq9fhi7s.jpg | 1 | 46 | P. putida | M9_cit | 0 |  | big
20/09/2021 | 186 | A00013ix92jm212l6ylfwbde15fbsv6.jpg | 1 | 46 | P. putida | M9_cit | 0 |  | big
20/09/2021 | 187 | A00013j1h6hl6qyf6mtsz2di6sow30q.jpg | 1 | 46 | P. putida | M9_cit | 0 |  | big
20/09/2021 | 188 | A00013mv5levsw9yel7wf3e1x82urvb.jpg | 1 | 46 | P. putida | M9_cit | 0 |  | big
20/09/2021 | 189 | A00013nit9tw2orcwdknvl3113zlp9o.jpg | 1 | 46 | P. putida | M9_cit | 0 |  | big
20/09/2021 | 190 | A00013nxy420utq8515za5tcqfpg64y.jpg | 1 | 46 | P. putida | M9_cit | 0 |  | big
20/09/2021 | 191 | A00013tkbpmp92uf7qtnsbiy2e58y6p.jpg | 1 | 46 | P. putida | M9_cit | 0 |  | big
20/09/2021 | 192 | A00013tmd0d93mc08idb4ua5av1e0tq.jpg | 1 | 46 | P. putida | M9_cit | 0 |  | big
20/09/2021 | 193 | A00013ueeeamn8wg6ya4yw7x5u37iq0.jpg | 1 | 46 | P. putida | M9_cit | 0 |  | big
20/09/2021 | 194 | A00013ufji91abkn2yamz043ji3izmx.jpg | 1 | 46 | P. putida | M9_cit | 0 |  | big
20/09/2021 | 195 | A00013vasrcam1jyg4lcnrj7d9bavz8.jpg | 1 | 46 | P. putida | M9_cit | 0 |  | big
20/09/2021 | 196 | A0001402cx1zvzouaporjsx7yaltunz.jpg | 1 | 2 | P. putida | M9_cit | 0 |  | big
20/09/2021 | 197 | A000142iwsiw75chdawmh1am1shfusz.jpg | 1 | 2 | P. putida | M9_cit | 0 |  | big
20/09/2021 | 198 | A0001476g8ec8v8g7vnigidtmuyd6p8.jpg | 1 | 2 | P. putida | M9_cit | 0 |  | big
20/09/2021 | 199 | A00014ba5nh4zlb9vsyq1juv8r79ocm.jpg | 1 | 2 | P. putida | M9_cit | 0 |  | big
20/09/2021 | 200 | A00014bxldg3e49zsjg7orj3mduspxk.jpg | 1 | 2 | P. putida | M9_cit | 0 |  | big
20/09/2021 | 201 | A00014e0assao8buu1h4tpa5bnl91h0.jpg | 1 | 2 | P. putida | M9_cit | 0 |  | big
20/09/2021 | 202 | A00014fhtjnfhf94tg9kq1nmplrne04.jpg | 1 | 2 | P. putida | M9_cit | 0 |  | big
20/09/2021 | 203 | A00014j9pl0zqpmjeqbile1l848ssbi.jpg | 1 | 2 | P. putida | M9_cit | 0 |  | big
20/09/2021 | 204 | A00014mi6ea4hs8pt3q3398vk3yxkhy.jpg | 1 | 2 | P. putida | M9_cit | 0 |  | big
20/09/2021 | 205 | A00014mspqoovsasp5f0qedtyjtl6ed.jpg | 1 | 2 | P. putida | M9_cit | 0 |  | big
20/09/2021 | 206 | A00014pavcvsaj9eni9afcpffqhl3o8.jpg | 1 | 2 | P. putida | M9_cit | 0 |  | big
20/09/2021 | 207 | A00014rodhdcnnbxqbo5z6q78p1a61x.jpg | 1 | 2 | P. putida | M9_cit | 0 |  | big
20/09/2021 | 208 | A00014u1xlv5s0ccl7vsga3fhw31m13.jpg | 1 | 2 | P. putida | M9_cit | 0 |  | big
20/09/2021 | 209 | A00014ud3tzg595uy4aho1yjj2cxgau.jpg | 1 | 2 | P. putida | M9_cit | 0 |  | big
20/09/2021 | 210 | A00014vwy2sdtjum8aazx4166zmeoq3.jpg | 1 | 2 | P. putida | M9_cit | 0 |  | big
20/09/2021 | 211 | A000150z6zhaysq81y721h3y2y2dvm5.jpg | 1 | 6 | P. putida | M9_cit | 0 |  | big
20/09/2021 | 212 | A0001540hn4um5oix7thte0poa722sb.jpg | 1 | 6 | P. putida | M9_cit | 0 |  | big
20/09/2021 | 213 | A000159e572vwixd54k3yoxsg8xl96s.jpg | 1 | 6 | P. putida | M9_cit | 0 |  | big
20/09/2021 | 214 | A00015avruzpin7ftn3wnnqyvtw62dq.jpg | 1 | 6 | P. putida | M9_cit | 0 |  | big
20/09/2021 | 215 | A00015buocx1hieiaexn7dn507151p6.jpg | 1 | 6 | P. putida | M9_cit | 0 |  | big
20/09/2021 | 216 | A00015d2me5c4hj9mkqd8ji111dw92l.jpg | 1 | 6 | P. putida | M9_cit | 0 |  | big
20/09/2021 | 217 | A00015flfbmq7wukd4f0exsw9attuw6.jpg | 1 | 6 | P. putida | M9_cit | 0 |  | big
20/09/2021 | 218 | A00015hm94xmbhjc4cvr6okwi1vatrl.jpg | 1 | 6 | P. putida | M9_cit | 0 |  | big
20/09/2021 | 219 | A00015jv84pay85dsotjzjh7pa9w59y.jpg | 1 | 6 | P. putida | M9_cit | 0 |  | big
20/09/2021 | 220 | A00015jyys9n7nqezvsgz4jutt37ez1.jpg | 1 | 6 | P. putida | M9_cit | 0 |  | big
20/09/2021 | 221 | A00015pbq284tfbwxxvcf4vngy1zmkq.jpg | 1 | 6 | P. putida | M9_cit | 0 |  | big
20/09/2021 | 222 | A00015qqd53boxfxbu7ov6stct1vzes.jpg | 1 | 6 | P. putida | M9_cit | 0 |  | big
20/09/2021 | 223 | A00015v3vqymo7ti84jwseeqgpxma89.jpg | 1 | 6 | P. putida | M9_cit | 0 |  | big
20/09/2021 | 224 | A00015w6k1ct4ku04lpb7ijjqhdiwg0.jpg | 1 | 6 | P. putida | M9_cit | 0 |  | big
20/09/2021 | 225 | A00015zst1l1rqjsjw42cfxzsblk0x9.jpg | 1 | 6 | P. putida | M9_cit | 0 |  | big
20/09/2021 | 226 | A000162xfkpwbydgyu7a86pb7cjouf9.jpg | 1 | 188 | P. putida | M9_cit | 0 | picked | big
20/09/2021 | 227 | A000164lycilfibbyjl1mezh6jc2xm8.jpg | 1 | 188 | P. putida | M9_cit | 0 | picked | big
20/09/2021 | 228 | A000167mjqimcxovt2dlk463cid6m7v.jpg | 1 | 188 | P. putida | M9_cit | 0 | picked | big
20/09/2021 | 229 | A000169csyhl22315d85c3hvlepeb60.jpg | 1 | 188 | P. putida | M9_cit | 0 | picked | big
20/09/2021 | 230 | A00016cjbc0p955sgvmd7rqi2t7523l.jpg | 1 | 188 | P. putida | M9_cit | 0 | picked | big
20/09/2021 | 231 | A00016es4xhbnz7x9jdn66t5n4xg7xo.jpg | 1 | 188 | P. putida | M9_cit | 0 | picked | big
20/09/2021 | 232 | A00016eufch9csr4rskto48404qby41.jpg | 1 | 188 | P. putida | M9_cit | 0 | picked | big
20/09/2021 | 233 | A00016g11t9jgnxebvr68ofm6vwtw3g.jpg | 1 | 188 | P. putida | M9_cit | 0 | picked | big
20/09/2021 | 234 | A00016jrz8erpszwge8k41domfa2w80.jpg | 1 | 188 | P. putida | M9_cit | 0 | picked | big
20/09/2021 | 235 | A00016nj2s0ope3wfzkf3xlqgopasui.jpg | 1 | 188 | P. putida | M9_cit | 0 | picked | big
20/09/2021 | 236 | A00016tx0vyb0ly37nxb3vwsjk4yesw.jpg | 1 | 188 | P. putida | M9_cit | 0 | picked | big
20/09/2021 | 237 | A00016uqg8uiohphu5pzilmp1syaf9k.jpg | 1 | 188 | P. putida | M9_cit | 0 | picked | big
20/09/2021 | 238 | A00016vzfuvyx3p34pxz6idu7rvgyjn.jpg | 1 | 188 | P. putida | M9_cit | 0 | picked | big
20/09/2021 | 239 | A00016ygql0yun5iucwn718ic1hwsw2.jpg | 1 | 188 | P. putida | M9_cit | 0 | picked | big
20/09/2021 | 240 | A00016zdofi1gxli3hfqlryg2n7g3lr.jpg | 1 | 188 | P. putida | M9_cit | 0 | picked | big
20/09/2021 | 241 | A0001759f6i21payh0slfquu4q74ag1.jpg | 1 | 303 | P. putida | M9_cit | 0 |  | big
20/09/2021 | 242 | A000175i5zy6ugfxjb5tccpzlt4srro.jpg | 1 | 303 | P. putida | M9_cit | 0 |  | big
20/09/2021 | 243 | A000178bkjz9yn6hvmmrr9q89dngi2q.jpg | 1 | 303 | P. putida | M9_cit | 0 |  | big
20/09/2021 | 244 | A00017ce0byxwx8ppm58nylvjriv6xb.jpg | 1 | 303 | P. putida | M9_cit | 0 |  | big
20/09/2021 | 245 | A00017hwrrs96kh36hvonytyebquflz.jpg | 1 | 303 | P. putida | M9_cit | 0 |  | big
20/09/2021 | 246 | A00017hxgyqzgouk3229h95ks0yb2f0.jpg | 1 | 303 | P. putida | M9_cit | 0 |  | big
20/09/2021 | 247 | A00017imskjdbck6a59wt8icf2x6gld.jpg | 1 | 303 | P. putida | M9_cit | 0 |  | big
20/09/2021 | 248 | A00017m2gejhfe4l81wgf1k98i5g7k5.jpg | 1 | 303 | P. putida | M9_cit | 0 |  | big
20/09/2021 | 249 | A00017pnn20etazdqq4ameth77xdk2l.jpg | 1 | 303 | P. putida | M9_cit | 0 |  | big
20/09/2021 | 250 | A00017qarm26yg8c3io0o8u7ves1jka.jpg | 1 | 303 | P. putida | M9_cit | 0 |  | big
20/09/2021 | 251 | A00017rb7tu3ncfpjigeo48i80xk4qn.jpg | 1 | 303 | P. putida | M9_cit | 0 |  | big
20/09/2021 | 252 | A00017stjpp1tp5feyz9bb71q1rix4i.jpg | 1 | 303 | P. putida | M9_cit | 0 |  | big
20/09/2021 | 253 | A00017wz49hvy78y2i5cje7vuizm7fv.jpg | 1 | 303 | P. putida | M9_cit | 0 |  | big
20/09/2021 | 254 | A00017yfkylrexb6xx8coi4yjp51weg.jpg | 1 | 303 | P. putida | M9_cit | 0 |  | big
20/09/2021 | 255 | A00017yhl6w3fhdlcmtpfpasi68orp7.jpg | 1 | 303 | P. putida | M9_cit | 0 |  | big
20/09/2021 | 256 | A000182kvpyawttq0tmzx478cz3qh5e.jpg | 1 | 523 | P. putida | M9_cit | 0 |  | small
20/09/2021 | 257 | A000182x33x90exv2612xuluo05f8er.jpg | 1 | 523 | P. putida | M9_cit | 0 |  | small
20/09/2021 | 258 | A0001834hg3zrpbiz5mi61dlw2hs9b0.jpg | 1 | 523 | P. putida | M9_cit | 0 |  | small
20/09/2021 | 259 | A000185j5kry8crv2ue156c4qvmtl80.jpg | 1 | 523 | P. putida | M9_cit | 0 |  | small
20/09/2021 | 260 | A0001862om3mo865dgg6qp5xqciosfi.jpg | 1 | 523 | P. putida | M9_cit | 0 |  | small
20/09/2021 | 261 | A000186zke35popbtgkk85z06gkaler.jpg | 1 | 523 | P. putida | M9_cit | 0 |  | small
20/09/2021 | 262 | A0001884p6ad69lafj744xpp8irowb1.jpg | 1 | 523 | P. putida | M9_cit | 0 |  | small
20/09/2021 | 263 | A000188uxs254vurq5qk43s2zuxfwzf.jpg | 1 | 523 | P. putida | M9_cit | 0 |  | small
20/09/2021 | 264 | A00018dmb46ls4kt2tojf08x63o7inq.jpg | 1 | 523 | P. putida | M9_cit | 0 |  | small
20/09/2021 | 265 | A00018e7h2xzyzan23t7f4kxq502c16.jpg | 1 | 523 | P. putida | M9_cit | 0 |  | small
20/09/2021 | 266 | A00018ewo5gvv8h64dcpnfuptdw4xc1.jpg | 1 | 523 | P. putida | M9_cit | 0 |  | small
20/09/2021 | 267 | A00018mdv14lomunigqf8tpppy7u1zf.jpg | 1 | 523 | P. putida | M9_cit | 0 |  | small
20/09/2021 | 268 | A00018mzrd6pn0ddkcxlgfmrl14p4q7.jpg | 1 | 523 | P. putida | M9_cit | 0 |  | small
20/09/2021 | 269 | A00018u01kneo5xy7i95aknibr2yokk.jpg | 1 | 523 | P. putida | M9_cit | 0 |  | small
20/09/2021 | 270 | A00018uxx0uw8jt4cz40lgv9isi44e0.jpg | 1 | 523 | P. putida | M9_cit | 0 |  | small
20/09/2021 | 271 | A000191prk5drmf0zsnlg0l00olum63.jpg | 1 | 36 | P. putida | M9_cit | 0 |  | big
20/09/2021 | 272 | A000196lbax2as1rqasrligueyqfwkb.jpg | 1 | 36 | P. putida | M9_cit | 0 |  | big
20/09/2021 | 273 | A000198h542uu160487qsb2a2mxtclg.jpg | 1 | 36 | P. putida | M9_cit | 0 |  | big
20/09/2021 | 274 | A00019979me31ulfmb3vv03a0s25a6k.jpg | 1 | 36 | P. putida | M9_cit | 0 |  | big
20/09/2021 | 275 | A00019ev2hreluhih3mf7bdqavh48ux.jpg | 1 | 36 | P. putida | M9_cit | 0 |  | big
20/09/2021 | 276 | A00019f7nv2k48g2pdf7qguhxam3xv4.jpg | 1 | 36 | P. putida | M9_cit | 0 |  | big
20/09/2021 | 277 | A00019i51omypkl1doccr85nhw3ds6z.jpg | 1 | 36 | P. putida | M9_cit | 0 |  | big
20/09/2021 | 278 | A00019j1qpyvfkq27vim60egdjbjlye.jpg | 1 | 36 | P. putida | M9_cit | 0 |  | big
20/09/2021 | 279 | A00019ovia4i63r3a20j414pm5z0auh.jpg | 1 | 36 | P. putida | M9_cit | 0 |  | big
20/09/2021 | 280 | A00019ql3sugks9rvznotjtu57iqmc3.jpg | 1 | 36 | P. putida | M9_cit | 0 |  | big
20/09/2021 | 281 | A00019sgrrpeifbffcbv4hwprfsow1g.jpg | 1 | 36 | P. putida | M9_cit | 0 |  | big
20/09/2021 | 282 | A00019xri62ylsxu0vs95pe6vhudixe.jpg | 1 | 36 | P. putida | M9_cit | 0 |  | big
20/09/2021 | 283 | A00019y0do46t7fsra0iqu8x67bza0e.jpg | 1 | 36 | P. putida | M9_cit | 0 |  | big
20/09/2021 | 284 | A00019ytk35xo2dhk88wry9c1esecgo.jpg | 1 | 36 | P. putida | M9_cit | 0 |  | big
20/09/2021 | 285 | A00019ywtv8e1gd778eqebotyjmafci.jpg | 1 | 36 | P. putida | M9_cit | 0 |  | big
20/09/2021 | 286 | A000201mwquzdbae38cytchjtw94gy2.jpg | 1 | 228 | P. putida | M9_cit | 0 |  | big
20/09/2021 | 287 | A000205bie65n89sc55igp3dgb3fvfx.jpg | 1 | 228 | P. putida | M9_cit | 0 |  | big
20/09/2021 | 288 | A000205coexx0jjb7apvzml66ga8q9v.jpg | 1 | 228 | P. putida | M9_cit | 0 |  | big
20/09/2021 | 289 | A000209ei14dgz4txya7j2gloltwy77.jpg | 1 | 228 | P. putida | M9_cit | 0 |  | big
20/09/2021 | 290 | A00020cpz66xyueqy9sogflmd0d4vf1.jpg | 1 | 228 | P. putida | M9_cit | 0 |  | big
20/09/2021 | 291 | A00020ewgw8023g7qs0wu3itpw9rmvz.jpg | 1 | 228 | P. putida | M9_cit | 0 |  | big
20/09/2021 | 292 | A00020jr9s6l3tu80cwhwajmsm052fe.jpg | 1 | 228 | P. putida | M9_cit | 0 |  | big
20/09/2021 | 293 | A00020kuqvef2k1de9n29f5bduaxu5h.jpg | 1 | 228 | P. putida | M9_cit | 0 |  | big
20/09/2021 | 294 | A00020kzdrr2n3dcv28f0m71p1lp032.jpg | 1 | 228 | P. putida | M9_cit | 0 |  | big
20/09/2021 | 295 | A00020m9zo1qk8rzh4txpzyq7240xhj.jpg | 1 | 228 | P. putida | M9_cit | 0 |  | big
20/09/2021 | 296 | A00020n1rzw60mpexem1tws4n2eugp2.jpg | 1 | 228 | P. putida | M9_cit | 0 |  | big
20/09/2021 | 297 | A00020nqv5oa9cevb4vozab6n5n0oof.jpg | 1 | 228 | P. putida | M9_cit | 0 |  | big
20/09/2021 | 298 | A00020nyf4v4wug4u1rxttqo77wsdj9.jpg | 1 | 228 | P. putida | M9_cit | 0 |  | big
20/09/2021 | 299 | A00020u0h1m76s843pbixn6h6sqelph.jpg | 1 | 228 | P. putida | M9_cit | 0 |  | big
20/09/2021 | 300 | A00020zkzh9710bffxlohzxjlnmm5a6.jpg | 1 | 228 | P. putida | M9_cit | 0 |  | big
20/09/2021 | 301 | A000210mqf3ir6our9g09id74b29090.jpg | 1 | 16 | P. putida | M9_cit | 0 |  | big
20/09/2021 | 302 | A000210ntph47yv3s9u2onpti60uwst.jpg | 1 | 16 | P. putida | M9_cit | 0 |  | big
20/09/2021 | 303 | A00021a7mei3kvepx1dr53af7zyap3h.jpg | 1 | 16 | P. putida | M9_cit | 0 |  | big
20/09/2021 | 304 | A00021ei837xzive41ne4x6dyorolud.jpg | 1 | 16 | P. putida | M9_cit | 0 |  | big
20/09/2021 | 305 | A00021ez8qgs7qlypb41d8gcwlbru86.jpg | 1 | 16 | P. putida | M9_cit | 0 |  | big
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

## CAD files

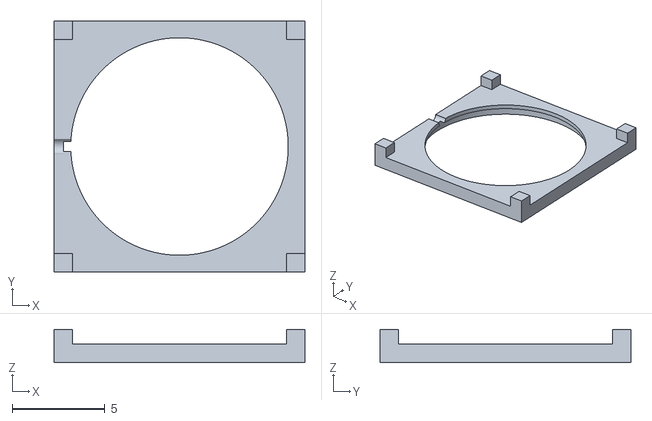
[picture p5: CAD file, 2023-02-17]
Computer Vision/Light frame CAD designs/lamp_holder.stl
13.5 x 13.5 x 1.80

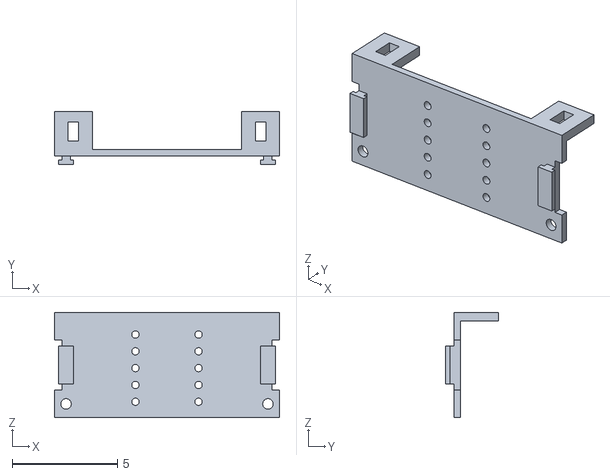
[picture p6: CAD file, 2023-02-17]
Framework assembly/hardware/stl files/Camera_adapter/cam_bracket.stl
10.7 x 2.50 x 5.00

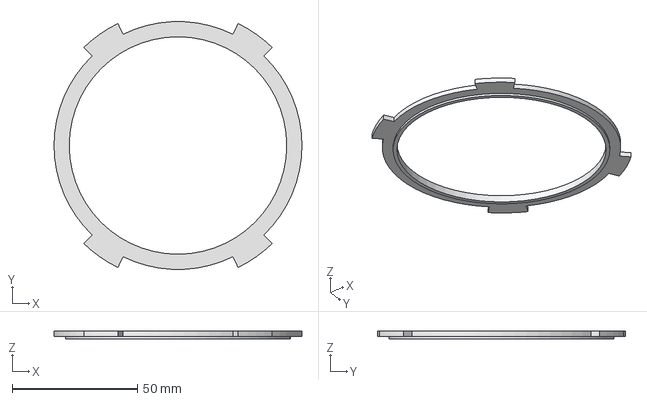
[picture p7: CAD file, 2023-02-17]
Framework assembly/hardware/stl files/Transilluminator/adaptor_petri_ring.stp
99.0 x 98.9 x 3.00 mm

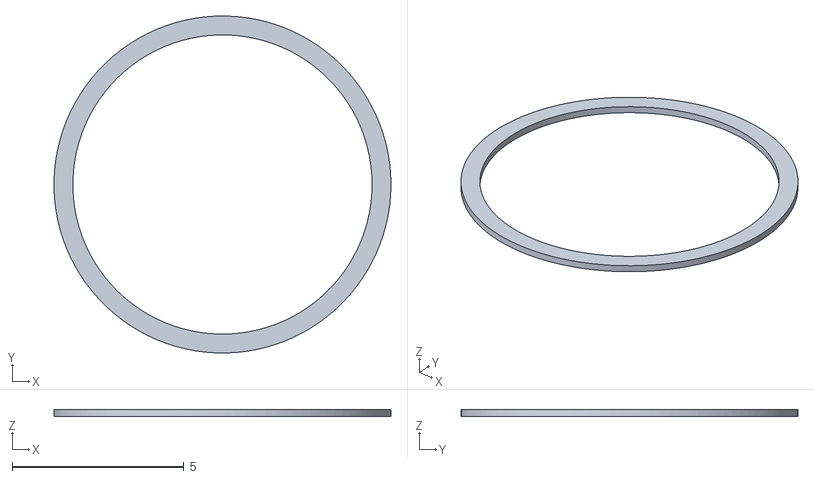
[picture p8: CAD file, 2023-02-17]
Computer Vision/Light frame CAD designs/lamp_holder_plate.stl
9.80 x 9.80 x 0.2

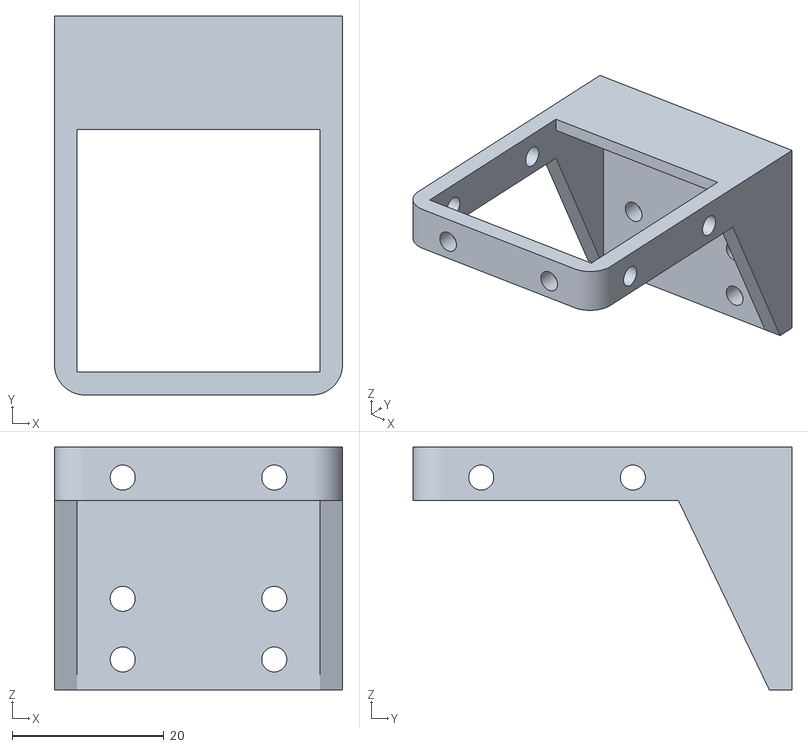
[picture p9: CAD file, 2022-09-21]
Framework assembly/hardware/stl files/Camera_adapter/cam_adapter_inv.stl
38.0 x 50.0 x 32.0

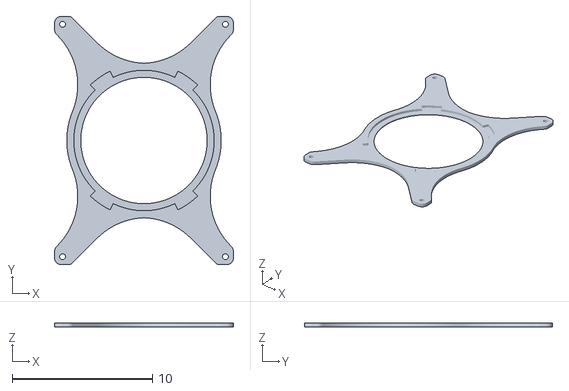
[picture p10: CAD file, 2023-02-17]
Framework assembly/hardware/stl files/Transilluminator/adaptor_petri.stl
12.8 x 17.7 x 0.3

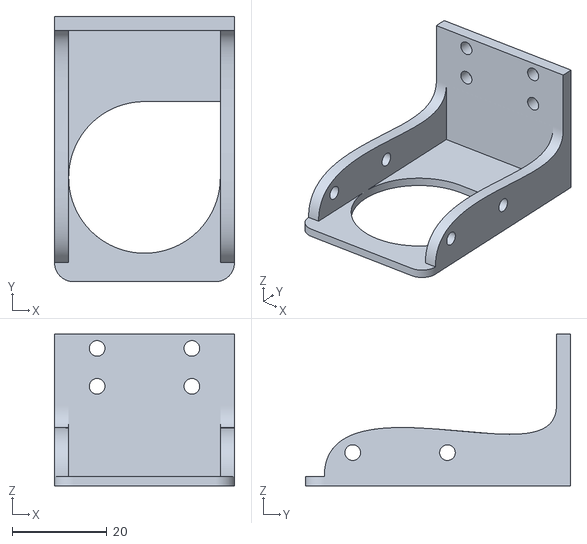
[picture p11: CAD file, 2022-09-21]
Framework assembly/hardware/stl files/Camera_adapter/cam_adapter_str.stl
38.0 x 56.0 x 32.0

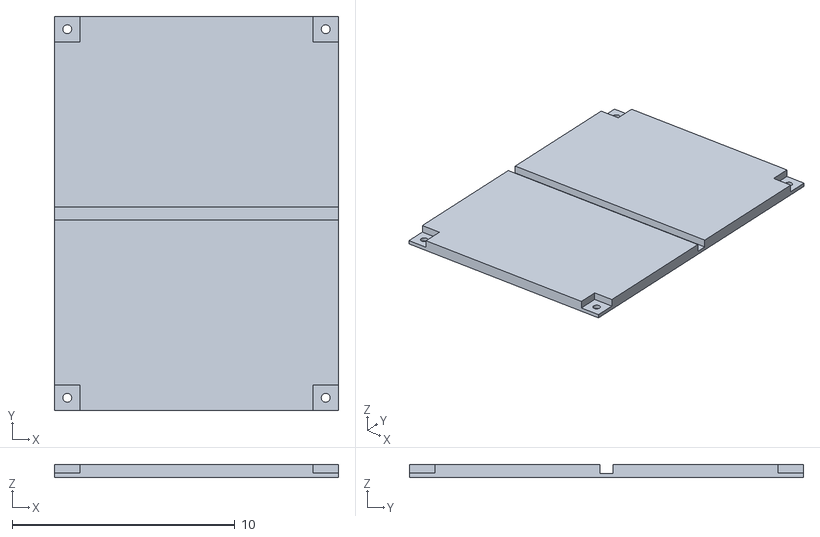
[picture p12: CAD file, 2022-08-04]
Framework assembly/hardware/stl files/Transilluminator/transillum_base_OT2_v1.stl
12.8 x 17.7 x 0.6

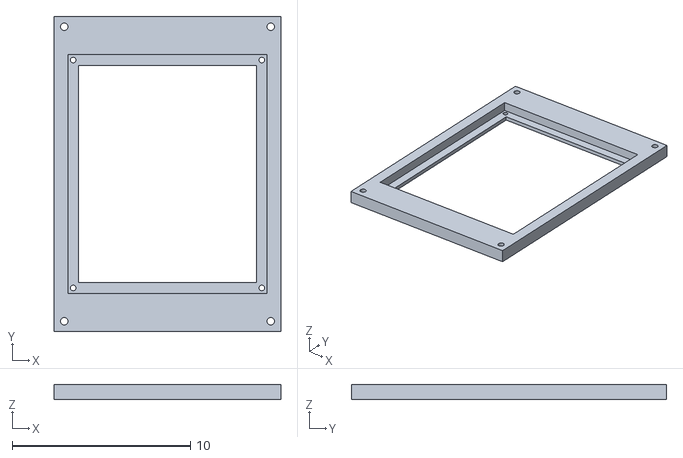
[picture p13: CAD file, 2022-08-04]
Framework assembly/hardware/stl files/Transilluminator/transillum_diffusor_holder_v1.stl
12.8 x 17.7 x 0.85

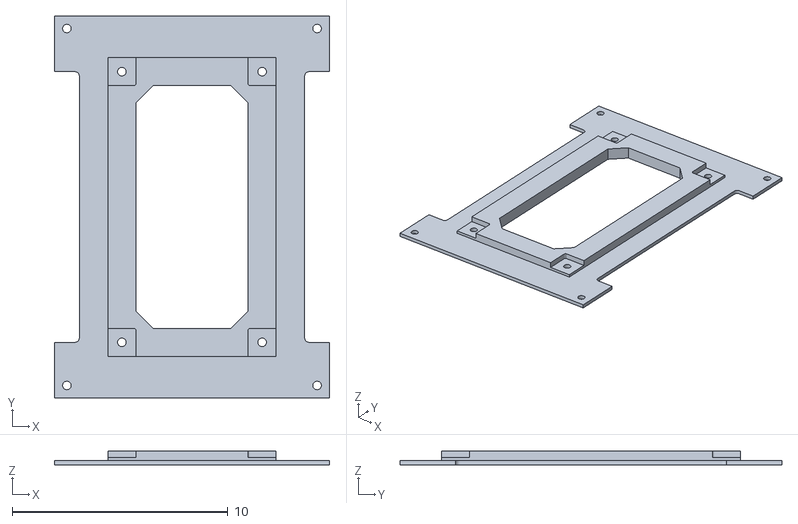
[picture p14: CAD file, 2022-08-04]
Framework assembly/hardware/stl files/Transilluminator/transillum_separator_v1.stl
12.8 x 17.7 x 0.65

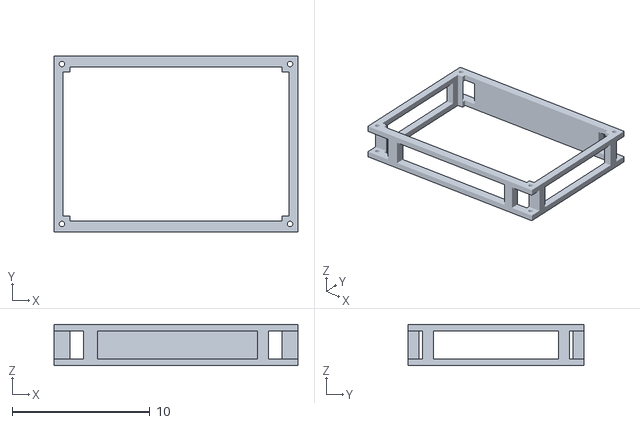
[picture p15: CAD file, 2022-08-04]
Framework assembly/hardware/stl files/Transilluminator/transillum_box_walls_v1.stl
17.7 x 12.8 x 3.00

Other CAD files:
Framework assembly/hardware/stl files/Transilluminator/adaptor_petri_ring.stl

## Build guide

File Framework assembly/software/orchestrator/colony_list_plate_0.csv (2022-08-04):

label | area | colony_robot_shift_x | colony_robot_shift_y
53 | 3146 | -17.282244406722146 | -13.381678049468023
27 | 3084 | -27.315867252359 | 7.329062643302239
52 | 2866 | -27.742422330682345 | -11.14722465471205
49 | 2414 | -10.775563930942747 | -9.138481025117063
20 | 2333 | 27.059077978393816 | 13.052671080527569
48 | 2289 | 38.221161831076756 | -7.348865159605591
45 | 2191 | 10.292205799940199 | -1.7871515204060338
14 | 2145 | -21.07531070042844 | 17.468688384098407
24 | 1892 | 22.89945251960734 | 11.34974312470664
46 | 1812 | -17.216740919480912 | -6.278506929197564
5 | 1734 | -17.205056050441748 | 24.680355565360056
50 | 1706 | -14.397378277306426 | -8.932400118020809
4 | 1524 | -7.261410179532016 | 24.892047318077818
38 | 1496 | -12.599966085043823 | 2.5682621397545193
12 | 1368 | -15.518320471008735 | 20.5466303544088
35 | 1325 | 14.725487952692024 | 3.8808792229953615
37 | 1208 | -7.127715753917995 | 2.948599031067334
8 | 1184 | 18.705658239280503 | 24.205029548339574
16 | 1176 | 20.010621670058214 | 16.993390110942993
32 | 1148 | 11.358337050844675 | 5.387327890933039
42 | 1074 | 4.86351883115729 | 1.346570979715082
19 | 1057 | -2.384719727427929 | 14.528976514511045
3 | 1055 | 15.123667469458544 | 25.462480874072888
43 | 1030 | 1.967126342140644 | 0.821695583500948
9 | 1014 | 3.991798411997596 | 23.176944005400184
26 | 995 | -2.4011956327825166 | 10.47708915719466
11 | 990 | 18.730740581622847 | 21.64302684563687
40 | 951 | -9.725434223845086 | 2.3939542904318256
6 | 817 | 9.450912984723615 | 24.830313993739683
28 | 806 | 4.911459721407788 | 7.717164810897418

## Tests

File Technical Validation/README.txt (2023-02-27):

Technical validation
-------------------

In order to validate the platform, we performed three different validation tests (raw picking test, color-based screening and fluorescence-based screening). Results of these experiments are included in the subfolders and detailed in the main manuscript of the implementation.

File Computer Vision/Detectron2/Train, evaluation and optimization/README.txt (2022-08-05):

**TRAIN, EVALUATION AND OPTIMIZATION**

# Workflow using the Colony Picking dataset (COPICK) in Detectron2 for training, evaluation and optimization tasks.

TRAINING, EVALUATION AND PANOPTIC PREDICTIONS 

	-"detectron2_train_eval.py": it is used for Detectron2 Config setup to perform model training and evaluation.

	-"detectron2_get_model_predictions.py": it is used to perform model inference on images that can be registered in a dataset or not and save the predictions.

	-"display_colonies_overlay.py": it is used to visualize the predicted colonies overlayed on top of the original image.

HYPERPARAMETERS OPTIMIZATION

	-"detectron2_optimization.py": it is used to perform model hyperparameters optimization in order to choose the best posible values to train and improve the Colony Picking panoptic model in Detectron2. Optimization is done using the library "Optuna" (https://optuna.org/).

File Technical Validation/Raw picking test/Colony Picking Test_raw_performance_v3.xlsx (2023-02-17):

Plate_number | File_name | Real colony number | Detectron 2 Segmented_colonies | True_positive | Noise / Artifacts deteced & picked | Colonies_in_groups_picked_as_single (counts) | Single_colonies_picked_as_group (counts) | objects_in_groups_picked_as_single (groups) | objects_picked_as_group (groups) | Not_processed | Not pickable (border) | Non detected
0 | ME3I_white__291122_095903 | 12 | 17 | 9 | 8 | 0 | 0 | 0 | 0 | 3 | 1 | 2
1 | ME3I_white__291122_131128 | 124 | 133 | 82 | 30 | 18 | 12 | 9 | 6 | 18 | 10 | 8
2 | ME3I_white__291122_162204 | 30 | 37 | 26 | 5 | 0 | 6 | 0 | 3 | 1 | 1 | 0
3 | ME3I_white__301122_111451 | 56 | 59 | 42 | 5 | 3 | 11 | 1 | 5 | 6 | 2 | 4
4 | ME3I_white__301122_115101 | 42 | 45 | 33 | 3 | 3 | 6 | 1 | 3 | 2 | 2 | 0
5 | ME3I_white__301122_120603 | 258 | 239 | 191 | 22 | 4 | 24 | 2 | 12 | 51 | 31 | 20
6 | ME3I_white__301122_134527 | 35 | 49 | 16 | 11 | 2 | 21 | 1 | 6 | 11 | 3 | 8
7 | ME3I_white__301122_152500 | 161 | 157 | 126 | 20 | 4 | 9 | 2 | 3 | 28 | 21 | 7
8 | ME3I_white__301122_154330 | 72 | 77 | 49 | 17 | 2 | 10 | 1 | 5 | 16 | 8 | 8
9 | ME3I_white__121222_113444 | 10 | 16 | 9 | 7 | 0 | 0 | 0 | 0 | 1 | 1 | 0
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

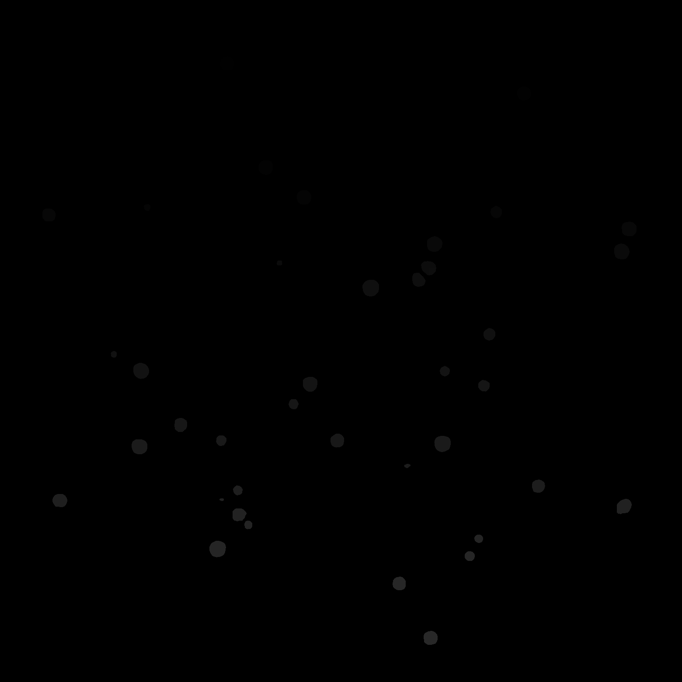
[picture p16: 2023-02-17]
Technical Validation/Raw picking test/ME3I_white__141222_170105__prediction.png

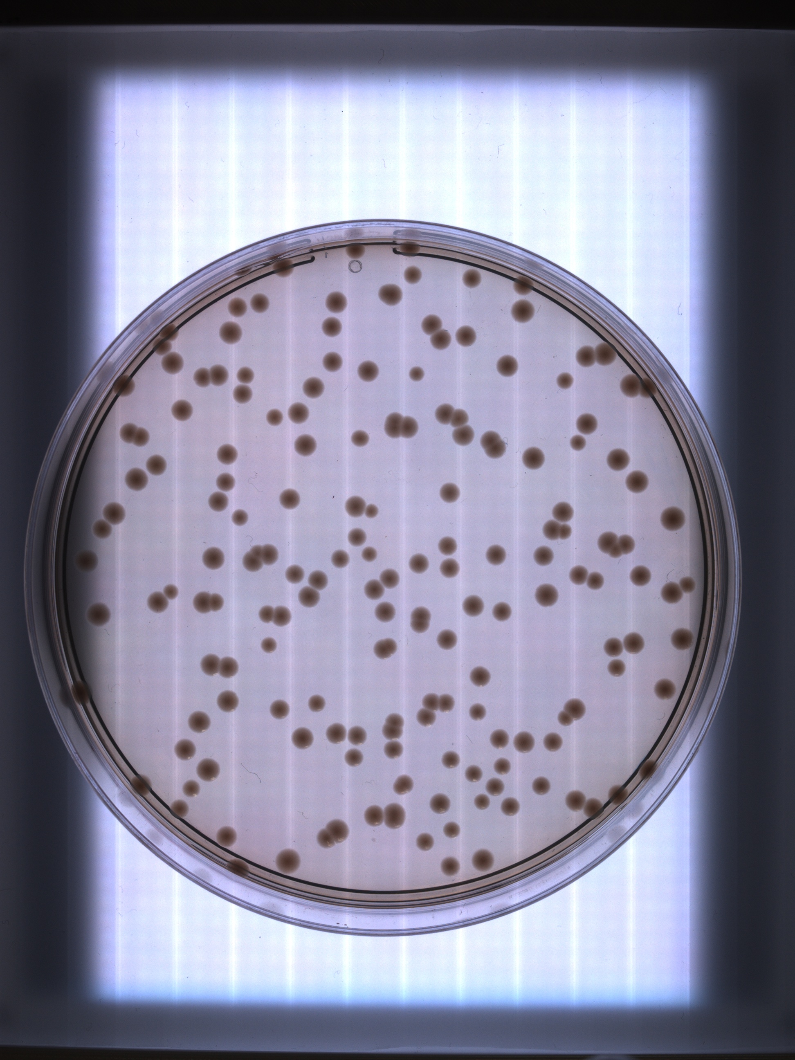
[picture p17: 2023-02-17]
Technical Validation/Raw picking test/ME3I_white__121222_152019.JPG

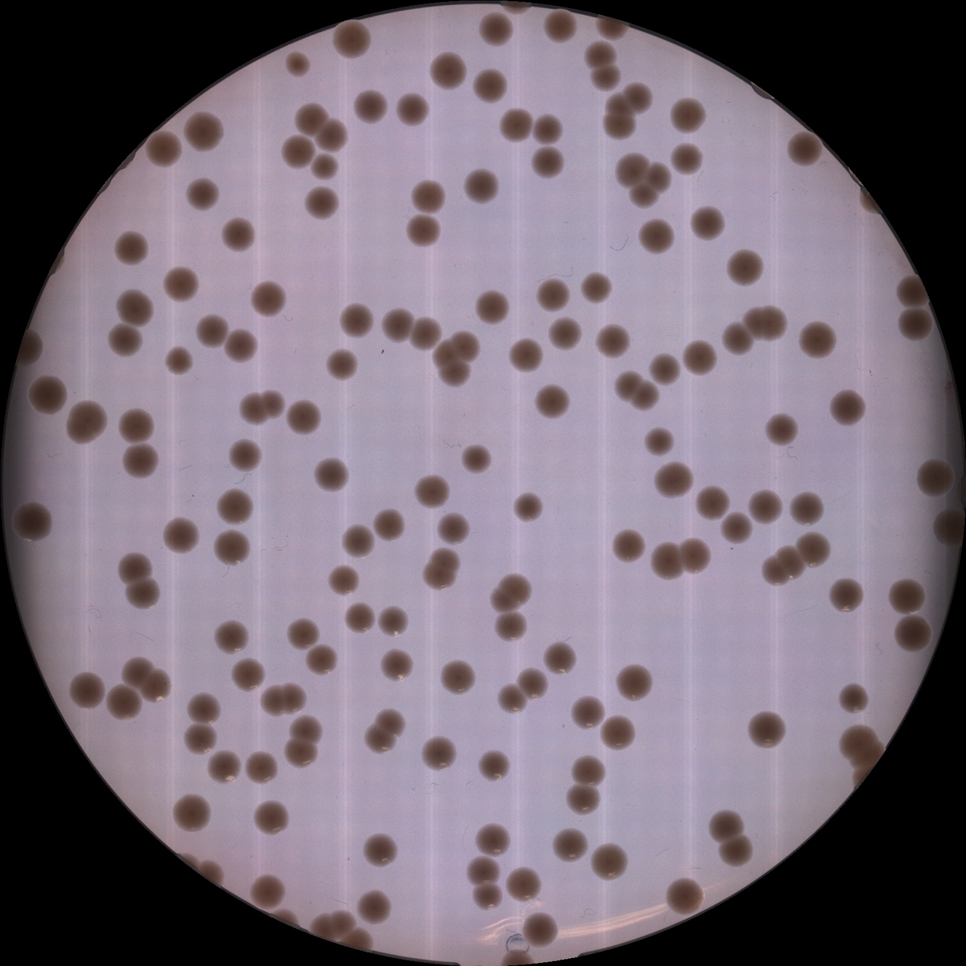
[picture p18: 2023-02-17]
Technical Validation/Raw picking test/ME3I_white__141222_152812_crop.JPG

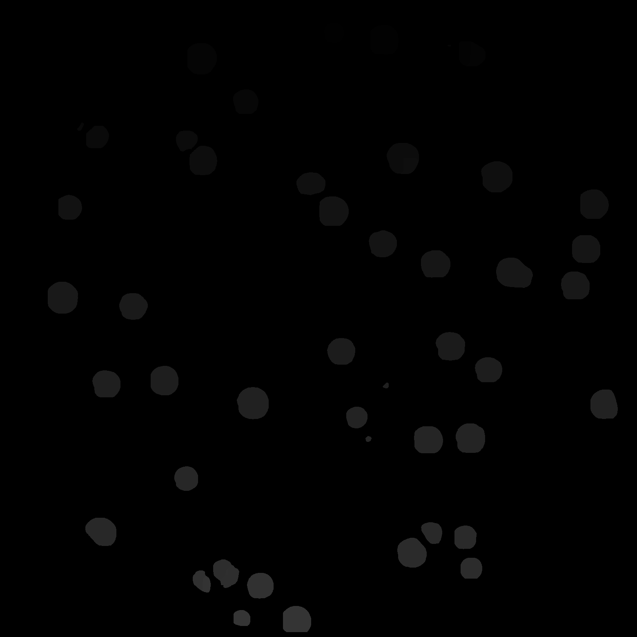
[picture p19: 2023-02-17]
Technical Validation/Raw picking test/ME3I_white__141222_200518__prediction.png

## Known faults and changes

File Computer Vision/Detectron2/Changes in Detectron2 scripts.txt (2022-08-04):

**CHANGES IN DETECTRON2 SCRIPTS**

# In our case, some parts of specific used functions in Detectron2 were modified in order to avoid recurrent errors while processing:

	Those modifications are:

	-In "visualizer.py" function (.../detectron2/utils/), line 490, we need to align our custom dataset categories indexes for visualization:

		text = self.metadata.stuff_classes[category_idx] --> (changed for) --> real_id=category_idx - 3  ## added (-3 because there are 3 stuff categories in the dataset with a reasigned contiguous id (just for visualization) and we want to access their real original ids as described in the dataset metadata)
            									       text = self.metadata.stuff_classes[real_id] ## added

	-In "functional.py" function (.../anaconda3/envs/detectron2_env/Lib/site-packages/torch/nn/), line 2846, target dtype changed in function call torch._C.nn.cross_entropy_loss():
		
		target --> (changed for) --> target.type(torch.long)

    	 	Because of error: "Expected type scalar long but got int". 

	-In "prepare_panoptic_fpn.py" function (.../detectron2/datasets/):

		Function "_process_panoptic_to_semantic.py" was separated in other file ("process_panoptic_to_semantic.py" in Dataset preparation folder) and modified:

			Instead of PIL Image library, we used Opencv to load and save the images.	

		Function "separate_coco_semantic_from_panoptic.py" was renamed ("separate_semantic_from_panoptic.py") and modified too:

			As there is no category_id==0 in the dataset, we commented id_map[thing_id]=0 in line 53. Further explanation available inside the function script.
